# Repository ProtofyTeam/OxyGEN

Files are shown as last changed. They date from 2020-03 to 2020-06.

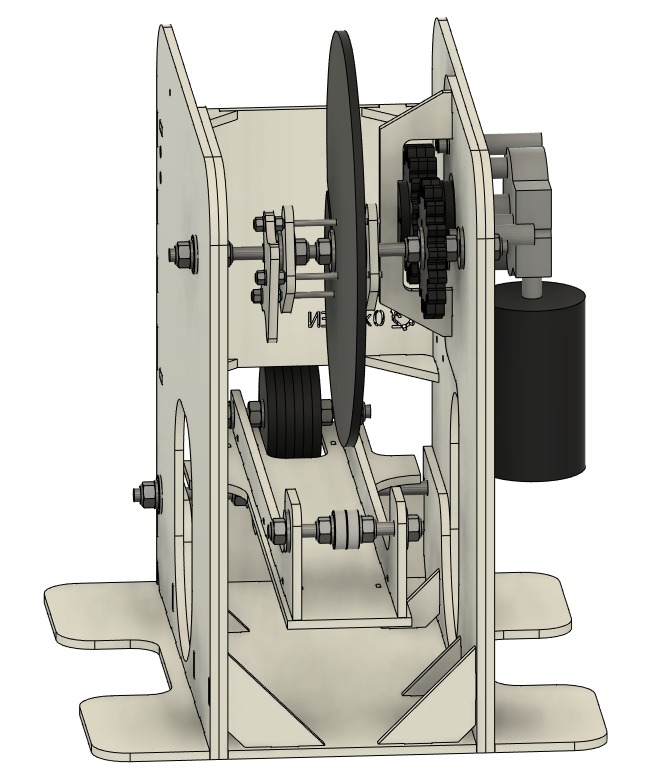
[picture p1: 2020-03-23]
oxygen_M/OxygenM_V5/OxygenM_V5 5mm/Images/f347e17a-e1d2-4af8-affd-06b3623857e8.jpeg

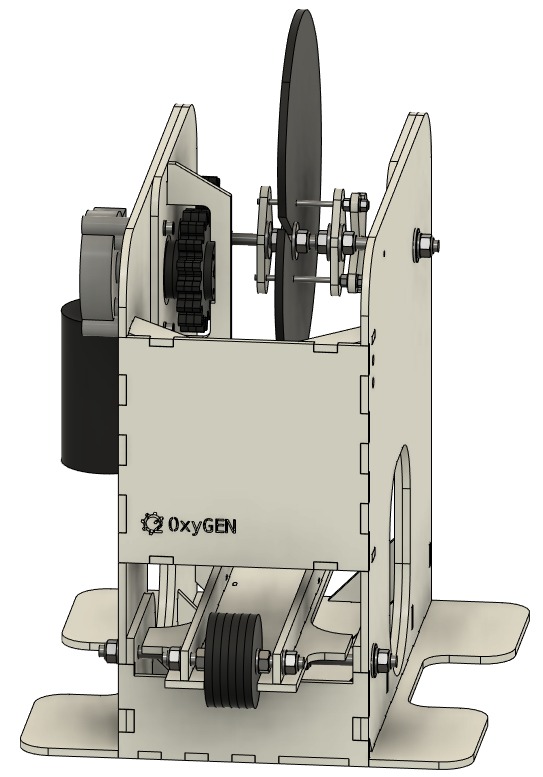
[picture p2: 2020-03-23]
oxygen_M/OxygenM_V5/OxygenM_V5 5mm/Images/4b5abb1e-1ea3-4c3a-8013-bc336fb86296.jpeg

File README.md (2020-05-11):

# OxyGEN

OxyGEN is a collaborative hardware project started and led by [Protofy.xyz](https://protofy.xyz/), a Barcelona-based company that supports innovation within Corps and SME’s by developing hardware and software solutions.

Our mission is to offer a chance of survival to those who are denied access to an artificial ventilator due to shortage of supply.

To fulfill this mission, OxyGEN created an open hardware, low cost and low tech emergency respirator using a manual resuscitator for emergency situations contributing to save lives.

There are 2 different versions of OxyGEN. The maker version "OxyGEN-M" and the industrial version "OxyGEN-IP".

* **OxyGEN-M** is designed for makers and can be built using common tools and no special machinery or materials are needed. 

* **OxyGEN-IP** is the version for industrial scale production. Foldforming metalworking machinery and engineering knowledge is needed to build OxyGEN-IP.

OxyGEN-IP has sucessfully passed clinical tests "in vitro" and "in vivo".

OxyGEN-IP has received authorization from the AEMPS to be used in clinical investigation in Hospital Clinic and Hospital Germans Trias i Pujol.

All content is licensed under the [CC by SA](https://creativecommons.org/licenses/by-sa/3.0)

**Important notice**

**OxyGEN is not a certified medical device. Always use OxyGEN under the supervision of qualified medical personnel. Incorrect use of the machine can result in serious injury or death.**

You can find all the information available on our [web](https://www.oxygen.protofy.xyz/?lang=es)

You can also find us at [Discord](https://discord.gg/yyYQxEG)

For any other questions, you can write to us at oxygen@protofy.xyz

-------------------------------------------------------------------------------------

OxyGEN es un proyecto colaborativo de hardware empezado y liderado por [Protofy.xyz](https://protofy.xyz/), una compañía barcelonesa que da soporte a la innovación en grandes empresas y Pymes desarrollando soluciones de hardware y software.

Nuestra misión es ofrecer una oportunidad de supervivencia a aquellos a los que se les ha denegado el acceso a un ventilador artificial debido a la escasez de suministro.

Para lograr esta misión, OxyGEN ha creado un respirador de emergencia de hardware libre, bajo coste y baja tecnología usando un resucitador manual para situaciones de emergencia, contribuyendo a salvar vidas.

Hay dos versiones diferentes de OxyGEN. La versión maker "OxyGEN-M" y la versión industrial "OxyGEN-IP".

* **OxyGEN-M** ha sido diseñado para ser construido por makers. No se necesitan herramientas especiales ni materiales caros. 

* **OxyGEN-IP** es la versión diseñada para la producción industrial a gran escala. Se necesita maquinaria industrial y conocimientos de ingeniería para construirla. 

OxyGEN-IP ha pasado satisfactoriamente pruebas de laboratorio "in vitro" e "in vivo". 

OxyGEN-IP ha recibido autorización de la AEMPS para su uso en estudios clínicos en el Hospital Clinic y el Hospital Germans Trias i Pujol.

Todo el contenido esta bajo licencia [CC by SA](https://creativecommons.org/licenses/by-sa/3.0)

**Nota Importante**

**OxyGEN no es un dispositivo médico certificado. No use OxyGEN sobre una persona, excepto bajo supervisión y aprobación médica. El uso incorrecto del aparato puede provocar lesiones graves o incluso la muerte. Usar OxyGEN en su país podría ser ilegal.**

Puedes encontrar toda la información disponible en nuestra [web](https://www.oxygen.protofy.xyz/?lang=es)

También puedes encontrarnos en [Discord](https://discord.gg/yyYQxEG)

Para cualquier otra consulta, puedes escribirnos a oxygen@protofy.xyz

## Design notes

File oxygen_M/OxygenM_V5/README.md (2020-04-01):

# OxyGEN V5

Mejoras:

- posibilidad de cambiar fácilmente las levas, para configurar los ritmos a respiraciones a diferentes tipos de pacientes

- integración de un DIMMER de leds que permite regular la velocidad del motor, para no depender los parámetros de cada motor en específico y poder ajustarlo a necesidades de paciente

- uso validado de un simple alimentación de PC (fuente ATX, 12v)

- varias horas de funcionamiento en continuo, comprobando la durabilidad del sistema

------------------------------------------------------------------------------------

Improvements:

- possibility to easily change the cams, to configure the rhythms to breaths for different types of patients

- integration of a LED DIMMER that allows regulating the motor speed, so as not to depend on the parameters of each specific motor and to be able to adjust it to patient needs

- validated use of a simple PC power supply (ATX source, 12v)

- several hours of continuous operation, checking the durability of the system

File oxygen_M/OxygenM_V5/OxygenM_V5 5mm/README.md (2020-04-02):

# OxyGEN V5 5mm

Diseño original de OxyGEN en 5mm

Esta version puede ser fabricada en acrilico, madera, chapa, o cualquier otro material rigido de 5mm que tenga suficiente resistencia como para aguantar la maquina y sus componentes.

Los planos estan diseñados para corte laser

------------------------------------------------------------------------------------

Original OxyGEN design in 5mm

This version can be made of acrylic, wood, sheet metal, or any other rigid 5mm material that has enough resistance to support the machine and its components.

The blueprints are designed for laser cutting

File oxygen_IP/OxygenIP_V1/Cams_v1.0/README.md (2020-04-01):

* XS = 450mL
* S = 500 mL
* M = 550 mL
* L = 600 mL
* XL = 650 mL

Se han publicado 3 sets de levas con relaciones de inspiración-espiración diferentes expresado como 1:N.

Set 1: Ratio 1:1

Set 2: Ratio 1:2

Set 3: Ratio 1:3

*En un pulmón sano y sin PEEP.

**Con una PEEP de 10 cm H2O una resistencia de 20 mbar/L/s y una complianza de 30 mL/mbar (valores para un pulmón muy dañado) los valores se verán reducidos en aproximadamente 120 mL

------------------------------------------------------------

3 sets of cams had been published with different inspiration-expiration time rates. Expressed as 1:N

Set 1: Rate 1:1

Set 2: Rate 1:2

Set 3: Rate 1:3

*In a healthy lung without PEEP.

**With a PEEP of 10 cm H2O a resistance of 20 mbar / L / s and a compliance of 30 ml / mbar (values for a badly damaged lung) the values will be reduced by approximately 120 ml

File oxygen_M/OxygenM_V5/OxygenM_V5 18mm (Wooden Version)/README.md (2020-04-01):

# OxyGEN V5 18mm

Se trata del diseño original V5 adaptado para ser fabricado con tablero de madera para poder fabricarlo con herramientas manuales y herrajes faciles de encontrar.

---------------------------------------------------

This is the original V5 design adapted to be made of wooden board so that it can be made with hand tools and easy-to-find hardware.

by Suso Caamanho

https://www.paoson.com/es/blog/respirador-manual-automatizado-n137

https://www.facebook.com/paosonwoodwork

https://www.youtube.com/user/gpaoson

https://www.instagram.com/paoson_woodworking/

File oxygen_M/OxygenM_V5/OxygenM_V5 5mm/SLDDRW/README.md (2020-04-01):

# OxyGEN v5 5mm version SLDDRW

Thanks to Neco!
https://www.linkedin.com/in/neco-garcía-quintanilla-690080166/

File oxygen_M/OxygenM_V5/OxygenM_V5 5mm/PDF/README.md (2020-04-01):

# OxyGEN v5 5mm version PDF's

Thanks to Neco!
https://www.linkedin.com/in/neco-garcía-quintanilla-690080166/

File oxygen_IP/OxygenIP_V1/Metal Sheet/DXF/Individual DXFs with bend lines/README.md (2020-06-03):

# Individual DXFs with bend lines

These are DXFs of the individual sheet metal parts with bend lines added for the bent parts.  The bend lines are on a separate layer named **Bending**.

One thing that was slightly changed from the originals was that the sets of three holes for the hinges on the **Outer Cover** and **Upper Cover** were moved 0.060 inch (1.52 mm) farther from the bend line to prevent the holes from "puckering" when the parts were bent.

These DXFs were created by [Kooima Company](https://www.kooimacompany.com/) for parts that were manufactured for the [Ventila](https://ventila.org/) organization in New York.

One thing to note is that, since metric thicknesses of stainless steel sheet are not so common in the USA, the following material substitutions were made:

**1mm:** Used 20 GA stainless steel (0.0375 in) (0.9525 mm)

**3mm:** Used 11 GA stainless steel (0.1250 in)	(3.175 mm)

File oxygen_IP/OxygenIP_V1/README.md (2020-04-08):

# OxyGEN IP V1.0

This version of OxyGEN is designed to be massively produced by manufactures willing to help.

------------------------------------------------------------------

Esta versión de OxyGEN está diseñada para ser producida masivamente por fabricantes dispuestos a ayudar.

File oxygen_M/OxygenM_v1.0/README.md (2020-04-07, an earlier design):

# OxyGEN V1.0

Primera versión de OxyGEN

Esta versión está pensada para producirse con herramientas de corte de madera básicas (sierra de mano, caladora...), usando madera de 20mm

-------------------------------------------

First version of OxyGEN

This version is designed to be produced with basic wood cutting tools (hand saw, jigsaw ...), using 20mm wood.

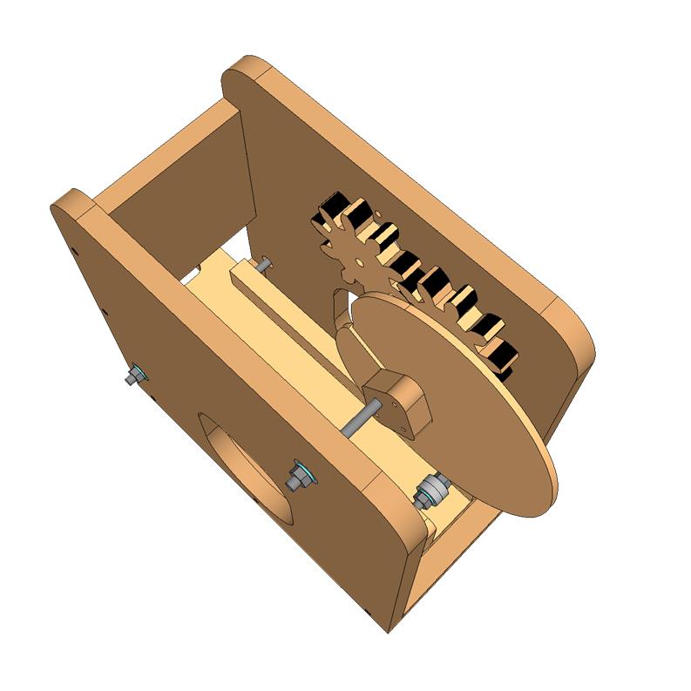
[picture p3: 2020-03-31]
oxygen_M/OxygenM_V5/OxygenM_V5 18mm (Wooden Version)/Photo/OxyGEN-master_Madera_Photo 2.jpg

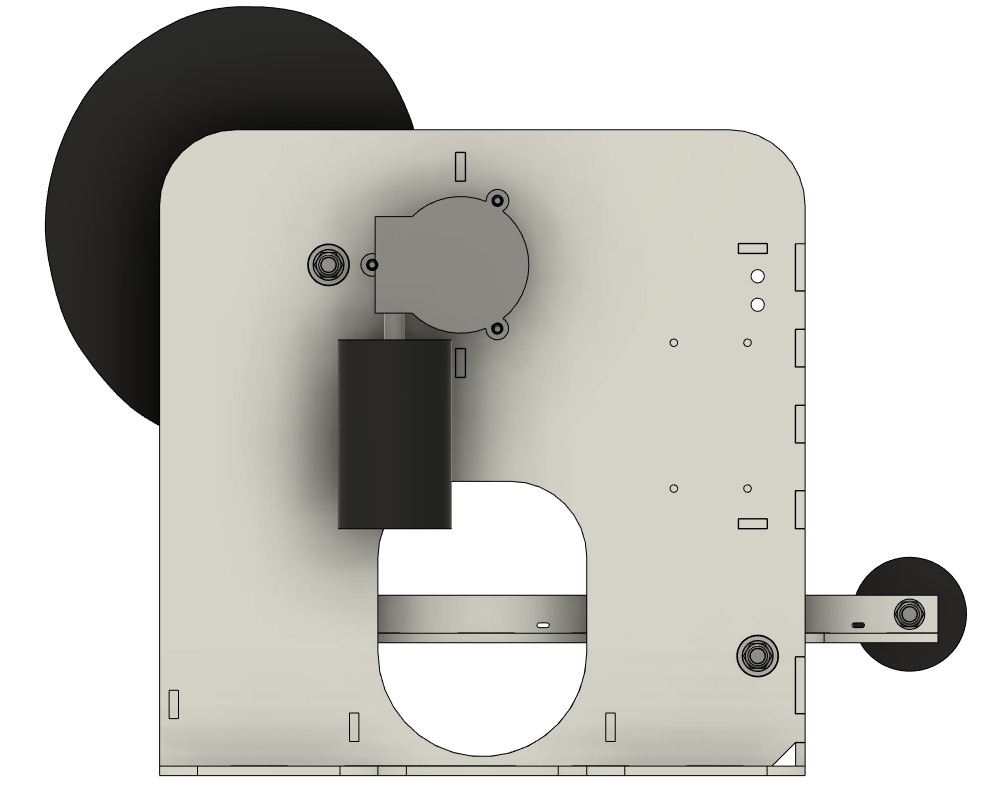
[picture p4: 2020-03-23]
oxygen_M/OxygenM_V5/OxygenM_V5 5mm/Images/67442de0-a628-4195-af0d-b7cb26ab55f8.jpeg

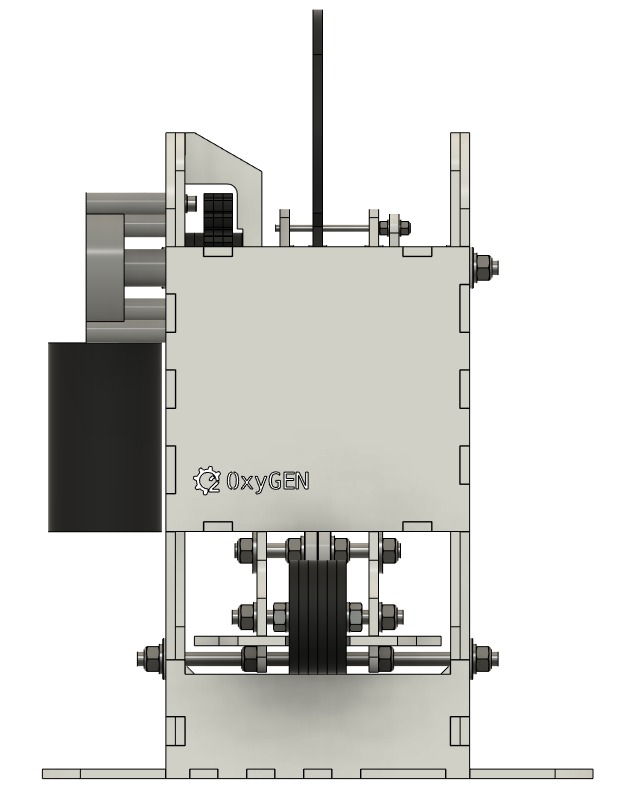
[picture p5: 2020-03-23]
oxygen_M/OxygenM_V5/OxygenM_V5 5mm/Images/628c36c9-1eaf-4945-878f-27b9a3d66050.jpeg

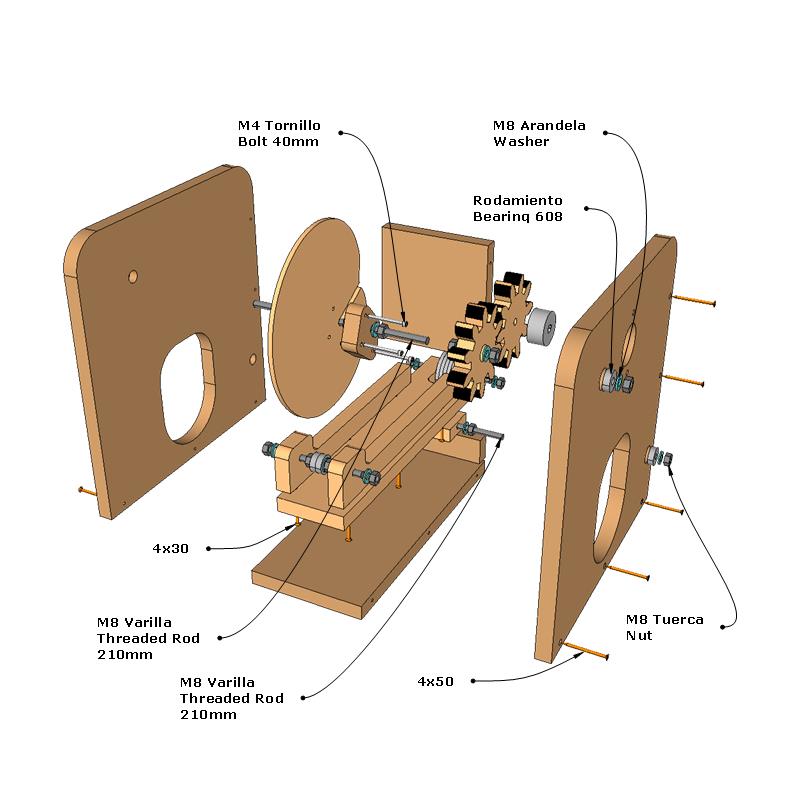
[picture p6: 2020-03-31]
oxygen_M/OxygenM_V5/OxygenM_V5 18mm (Wooden Version)/Photo/OxyGEN-master_Madera_Fasteners.jpg

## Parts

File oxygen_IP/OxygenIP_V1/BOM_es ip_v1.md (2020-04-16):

# Lista de materiales necesarios para IP_v1:

* 1	Chapa Inox 1 mm	
* 1	Chapa Inox 3 mm	
* 1	Chapa Inox 5 mm	
* 1	Plancha Metacrilato 5 mm x 485,5 mm x 160 mm	
* 1	Plancha Nylon/Delrin/PVC 10 mm x 50 mm x 42 mm	
* 1	Barra Inox Ø12 mm x 158 mm 	
* 1	Barra Inox Ø16 mm x 170 mm	
* 1	Barra Inox Ø50 mm x 20 mm	
* 1	Barra Nylon/Delrin Ø10,5 mm x 51 mm
* 3	Barra Nylon/Delrin Ø12 mm x 43,5 mm	
* 1	Barra Nylon/Delrin Ø22 mm x 105 mm	
* 1	Barra Nylon/Delrin Ø50 mm x 52 mm	
* 1	Liston Nylon/Delrin 42 mm x 33 mm x 105 mm	
* 1	Liston Nylon/Delrin 70 mm x 24,8 mm x 305 mm	
* 2	Pasador Metálico Ø6 mm x 23 mm	
* 1	Manómetro	
* 4	Rodamiento Ø37 mm x 12 mm	
* 1	Motor 12V 48W 6Nm 30RPM REF.11194592000E	
* 1	Fuente PC ATX 500W	
* 1	Dimmer LED 12/24V 8A	
* 2	Final de carrera	
* 1	Luz de funcionamiento 230V AC 5W	
* 1	Tapón Ø40 mm	
* 1	Diodo Schottky Imax ≥ 5 A, Pd(25ºC) ≥ 5 W	
* 1	Conector Alimentación IEC C14 con Interruptor y Fusible	
* 1	Cable Alimentación IEC C13 a Faston	
* 1	Cable AWG 16 Aprox. 1 m	
* 6	Tuerca M3 	
* 7	Tuerca M5	
* 5	Tuerca Remachada M5	
* 2	Tapex M10
* 2	Tornillo DIN 912 M3 x 15 mm	
* 4	Tornillo DIN 912 M3 x 16 mm	
* 1	Tornillo DIN 912 M5 x 40 mm	
* 3	Tornillo DIN 912 M6 x 50 mm	
* 4	Tornillo M6 x 24 mm	
* 2	Tornillo M10 x 20 mm	
* 6	Tornillo Roscachapa M4 x 10 mm	
* 12 	Tornillo Roscachapa M5 x 12	mm
* 8	Tornillo Roscachapa M5 x 20 mm	
* 47 	Remache Ø4,8 mm
* 1	Hembrilla Rosca Ø4 mm x 18 mm, enganche ØInterior 8 mm	 
* 2	Bisagra 60 mm x 50 mm	
* 1	Muelle ØInterior 9 mm x 90 mm	
* 1	Muelle ØInterno 12mm x 31 mm 	
* 1	Junta Tórica ØExterior 30 mm, ØInterior 22 mm	
* 10 	Separador de goma para agujero Ø15,5, separación 6 mm	
* 1	Separador Nylon ØExterior 20 mm, ØInterior 13 mm, 29 mm	
* 1	Separador Nylon ØExterior 20 mm, ØInterior 13 mm, 35 mm	
* 1	Espuma Aislante 6 mm x 171 mm x 45 mm	
* 2	Goma Protectora Longitud Aprox. 460 mm 	
* 2	Goma Protectora Grosor 2.5 mm Longitud Aprox. 1125 mm	
* 1	Acoplador del Motor de Ø12 mm a Ø10 mm, longitud 35 mm	
* 1	Casquillo de Bronce Ø16 mm x 70 mm

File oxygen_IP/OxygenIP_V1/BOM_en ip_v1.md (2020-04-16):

# Bill Of Material for  IP_v1:

* 1	Inox Sheet 1 mm	
* 1	Inox Sheet 3 mm	
* 1	Inox Sheet 5 mm	
* 1	Methacrylate Sheet 5 mm x 485,5 mm x 160 mm	
* 1	Nylon/Delrin/PVC Sheet 10 mm x 50 mm x 42 mm	
* 1	Inox Bar Ø12 mm x 158 mm 	
* 1	Inox Bar Ø16 mm x 170 mm	
* 1	Inox Bar Ø50 mm x 20 mm	
* 1	Nylon/Delrin Bar Ø10,5 mm x 51 mm
* 3	Nylon/Delrin Bar Ø12 mm x 43,5 mm	
* 1	Nylon/Delrin Bar Ø22 mm x 105 mm	
* 1	Nylon/Delrin Bar Ø50 mm x 52 mm	
* 1	Nylon/Delrin Batten 42 mm x 33 mm x 105 mm	
* 1	Nylon/Delrin Batten 70 mm x 24,8 mm x 305 mm	
* 2	Metal Pin Ø6 mm x 23 mm	
* 1	Manometer	
* 4	Bearing Ø37 mm x 12 mm	
* 1	Motor 12V 48W 6Nm 30RPM REF.11194592000E	
* 1	PC Power Supply ATX 500W	
* 1	Dimmer LED 12/24V 8A	
* 2	Micro Switch
* 1	Operating Light 230V AC 5W	
* 1	Plug Ø40 mm	
* 1	Schottky Diode Ifmax ≥ 5 A, Pd(25ºC) ≥ 5 W	
* 1	Power Connector IEC C14 with Switch and Fuse	
* 1	Power Cable IEC C13 to Faston	
* 1	Cable AWG 16 Approx. 1 m	
* 6	Nut M3 	
* 7	Nut M5	
* 5	Rivet Nut M5	
* 2	Tapex M10
* 2	Screw DIN 912 M3 x 15 mm	
* 4	Screw DIN 912 M3 x 16 mm	
* 1	Screw DIN 912 M5 x 40 mm	
* 3	Screw DIN 912 M6 x 50 mm	
* 4	Screw M6 x 24 mm	
* 2	Screw M10 x 20 mm	
* 6	Self Tapping Screw M4 x 10 mm	
* 12 	Self Tapping Screw M5 x 12 mm
* 8	Self Tapping Screw M5 x 20 mm	
* 47 	Rivet Ø4,8 mm
* 1	Eyebolt Thread Ø4 mm x 18 mm, hitch ØIn 8 mm	 
* 2	Hinge 60 mm x 50 mm	
* 1	Spring ØIn 9 mm x 90 mm	
* 1	Spring ØIn 12mm x 31 mm 	
* 1	O-ring ØEx 30 mm, ØIn 22 mm	
* 10 	Rubber hole spacer Ø15,5, separation 6 mm	
* 1	Nylon Spacer ØEx 20 mm, ØIn 13 mm, 29 mm	
* 1	Nylon Spacer ØEx 20 mm, ØIn 13 mm, 35 mm	
* 1	Foam 6 mm x 171 mm x 45 mm	
* 2	Protective rubber length Approx. 460 mm 	
* 2	Protective rubber thickness 2.5 mm length Approx. 1125 mm	
* 1	Motor coupling from Ø12 mm to Ø10 mm, length 35 mm	
* 1	Bronze Bearing Ø16 mm x 70 mm

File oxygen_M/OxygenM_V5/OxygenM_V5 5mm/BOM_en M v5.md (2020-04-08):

#Bill Of Material for V5M:

 * 2 threaded rod M8 190mm
 * 2 M8 90mm threaded rod
 * 3 threaded rod M4 71mm
 * 21 Locking nut M8
 * 2 Nut M8
 * 10 M8 washer
 * 12 M8 wide washer
 * 10 Locking nut
 * 14 M4 washer
 * 3 M6 15mm Screw
 * 3 M6 washer
 * 6 Bearing 22m
 * 12 / 24V LED dimmer with 8A max.
 * Wiper motor 12v 48W 6Nm 30rpm max (We have used the DOGA model 11194592000E)
 * PC ATX 500w source
 * Super glue
 * Imax Diode> = 150A Pd (25º)> = 5W
 * 1m AWG 16 Cable
 * Acrylic sheet 5mm 0.95m x 1.2m

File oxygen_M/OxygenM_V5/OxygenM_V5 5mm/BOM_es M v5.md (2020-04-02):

# Lista de materiales necesarios para V5M:

 * 2 varilla roscada M8 190mm
 * 2 varilla roscada M8 90mm
 * 3 varilla roscada M4 71mm
 * 21 Tuerca bloqueante M8
 * 2 Tuerca M8 
 * 10 Arandela M8
 * 12 Arandela ancha M8
 * 10 Tuerca bloqueante
 * 14 Arandela M4
 * 3 Tornillo M6 15mm
 * 3 Arandela M6
 * 6 Rodamiento 22m
 * Dimmer LED 12/24V con 8A max
 * Motor limpiaparabrisas 12v 48W 6Nm 30rpm max (Nosotros hemos usado el modelo 11194592000E de DOGA)
 * Fuente PC ATX 500w
 * Superglue
 * Diodo Imax >= 150A Pd(25º)>= 5W
 * 1m Cable AWG 16
 * Plancha metacrilato 5mm 0.95m x 1.2m

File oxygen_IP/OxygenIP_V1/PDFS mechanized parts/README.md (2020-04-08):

Muchas gracias a nuestros amigos de OxyGEN Brasil!

https://www.facebook.com/Volunt%C3%A1rios-An%C3%B4nimos-Ventilador-Oxygen-110522390598983

------------------------------------------------------------------

Thank you very much to our friends from OxyGEN Brazil!

https://www.facebook.com/Volunt%C3%A1rios-An%C3%B4nimos-Ventilador-Oxygen-110522390598983

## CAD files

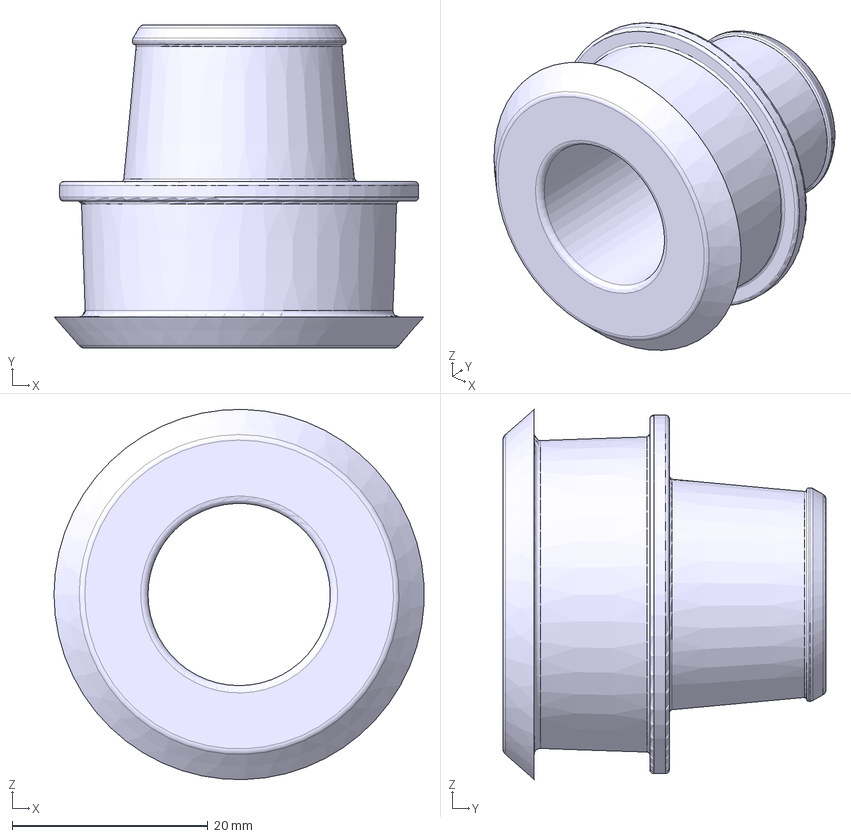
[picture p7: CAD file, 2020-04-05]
accessories/spur back to tube.step
37.8 x 33.0 x 37.8 mm

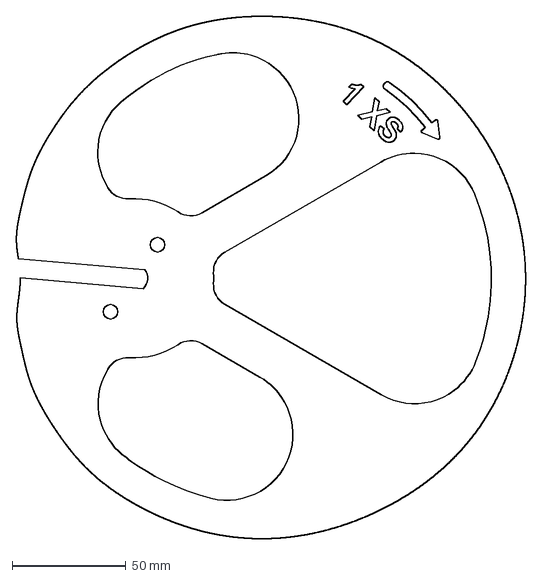
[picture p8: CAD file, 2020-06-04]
oxygen_IP/OxygenIP_V1/Cams_v1.0/Set 1/1-1 89-205-50-XS-v8.dxf
223.9 x 229.8 mm

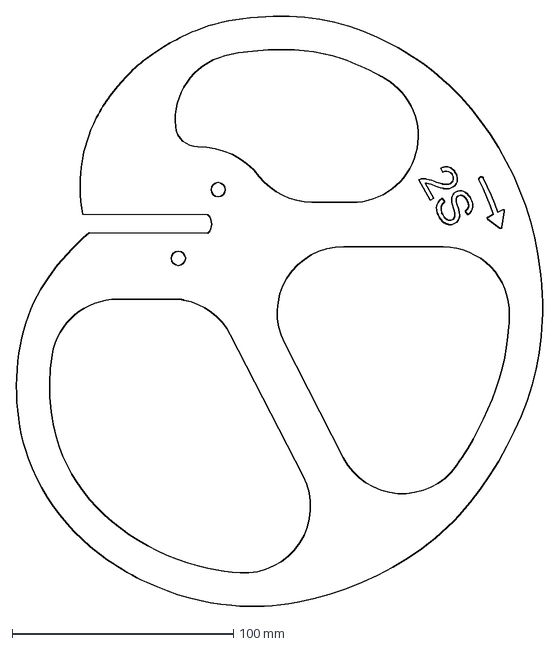
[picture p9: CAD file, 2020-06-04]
oxygen_IP/OxygenIP_V1/Cams_v1.0/Set 2/1-2 83-205-50-S-v8.dxf
238.2 x 267.0 mm

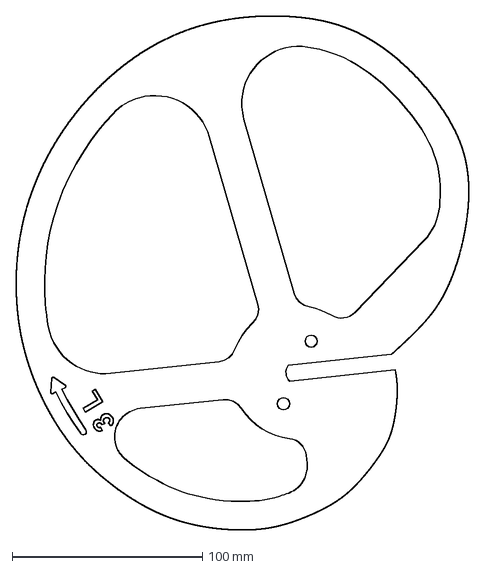
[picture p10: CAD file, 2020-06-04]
oxygen_IP/OxygenIP_V1/Cams_v1.0/Set 3/1-3 71-205-50-L-v8.dxf
238.1 x 270.3 mm

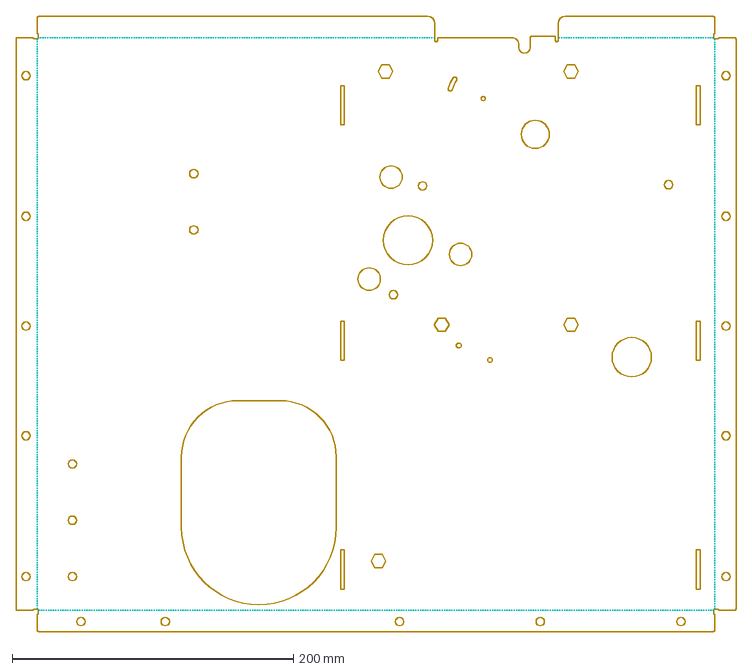
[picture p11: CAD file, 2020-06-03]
oxygen_IP/OxygenIP_V1/Metal Sheet/DXF/Individual DXFs with bend lines/1mm/Central Cover.dxf
511.8 x 437.3 mm

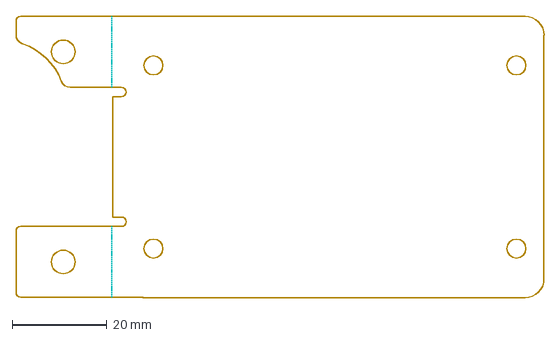
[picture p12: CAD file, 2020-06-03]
oxygen_IP/OxygenIP_V1/Metal Sheet/DXF/Individual DXFs with bend lines/3mm/Dimmer Support.dxf
111.7 x 59.5 mm

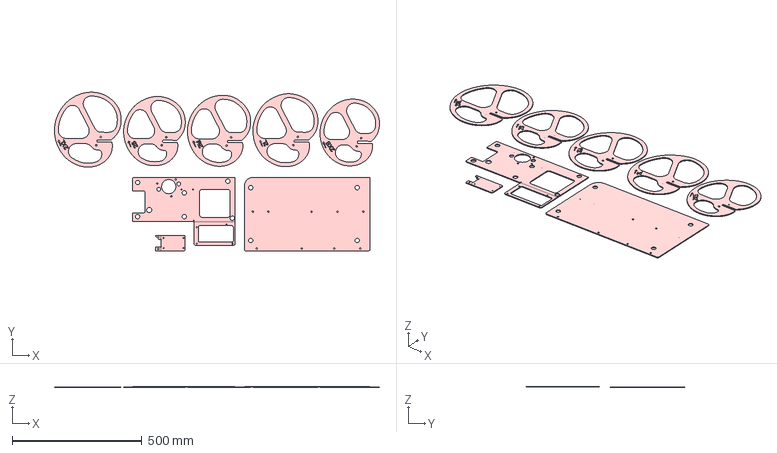
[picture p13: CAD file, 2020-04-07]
oxygen_IP/OxygenIP_V1/Metal Sheet/STEP/Oxygen-IP V14.4 Metal Sheet 3 mm Parts.step
1253.3 x 611.8 x 5.00 mm

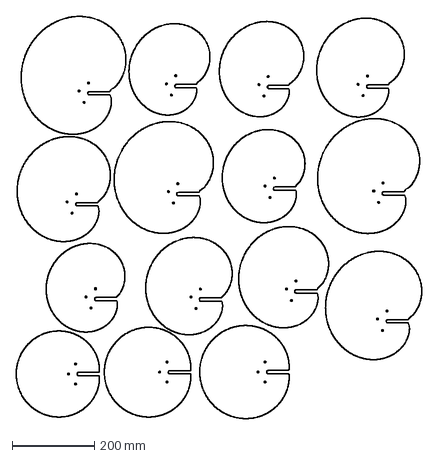
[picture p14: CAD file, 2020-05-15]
oxygen_M/OxygenM_V5/OxygenM_V5 5mm/cams/OXyGEN_V5_M_cams.dxf
983.3 x 975.3 mm

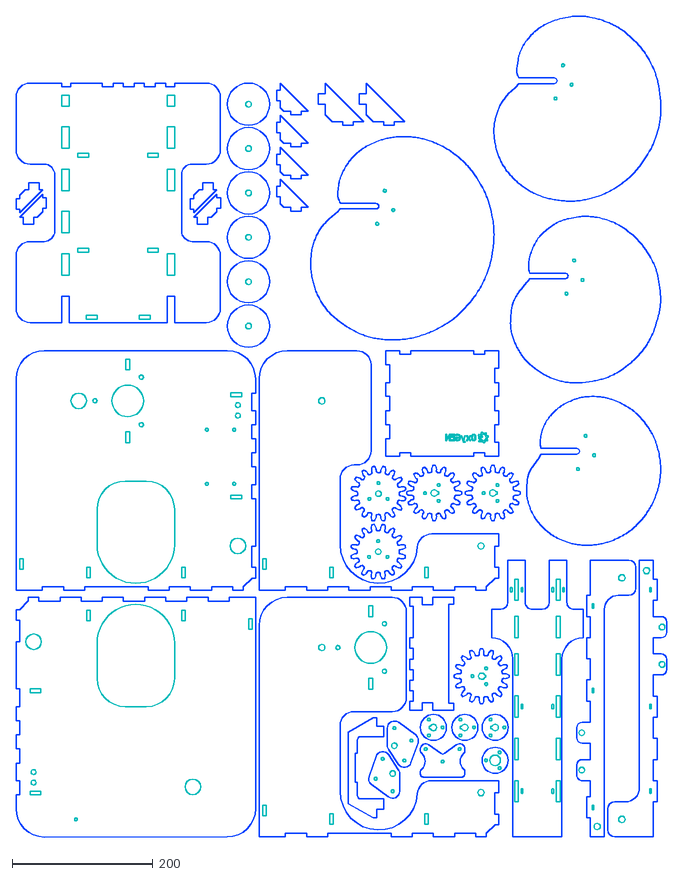
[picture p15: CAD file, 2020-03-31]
oxygen_M/OxygenM_V5/OxygenM_V5 5mm/DXF/OxyGEN_Maker_V5.dxf
924.0 x 1165.5

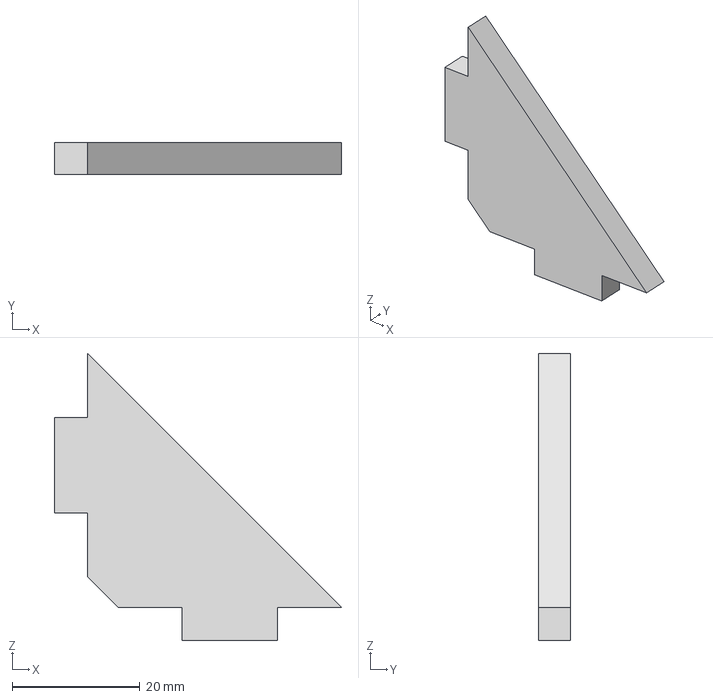
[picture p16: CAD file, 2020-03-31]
oxygen_M/OxygenM_V5/OxygenM_V5 5mm/STEP/Oxygen Maker Escuadra Frontal 4.step
45.0 x 5.00 x 45.0 mm

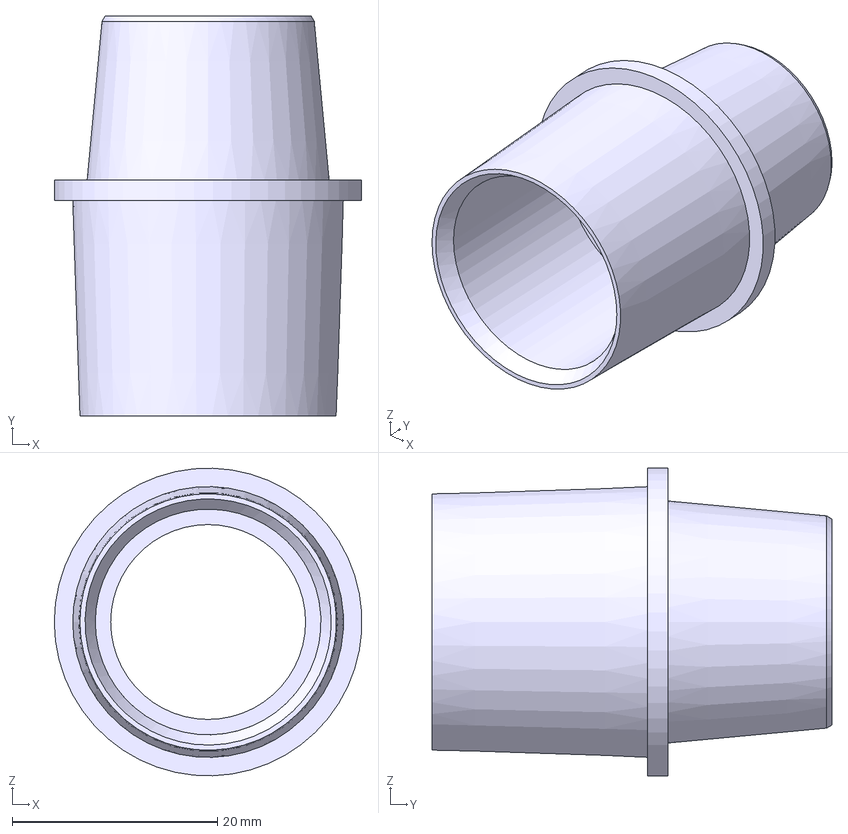
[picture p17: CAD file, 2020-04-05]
accessories/tube to spur valve.step
30.0 x 39.0 x 30.0 mm

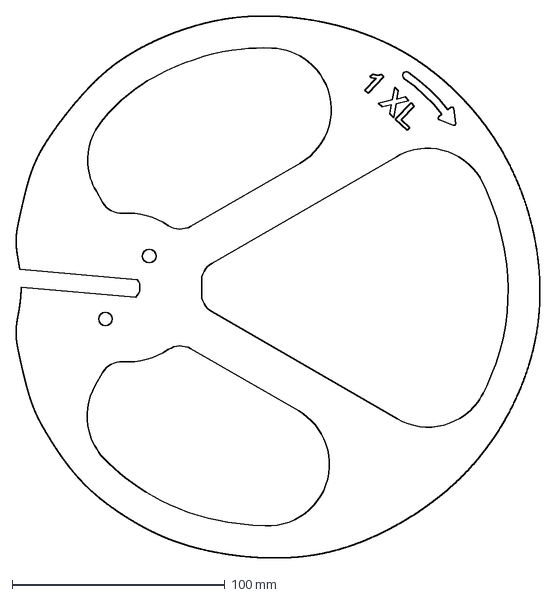
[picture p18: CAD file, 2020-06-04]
oxygen_IP/OxygenIP_V1/Cams_v1.0/Set 1/1-1 65-205-50-XL-v8.dxf
246.5 x 255.0 mm

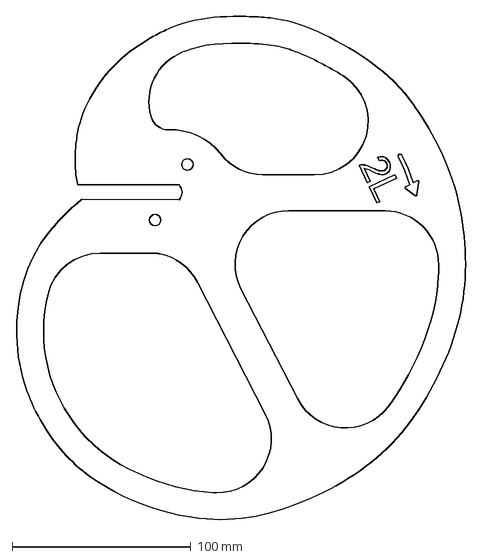
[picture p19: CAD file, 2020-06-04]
oxygen_IP/OxygenIP_V1/Cams_v1.0/Set 2/1-2 71-205-50-L-v8.dxf
251.3 x 281.6 mm

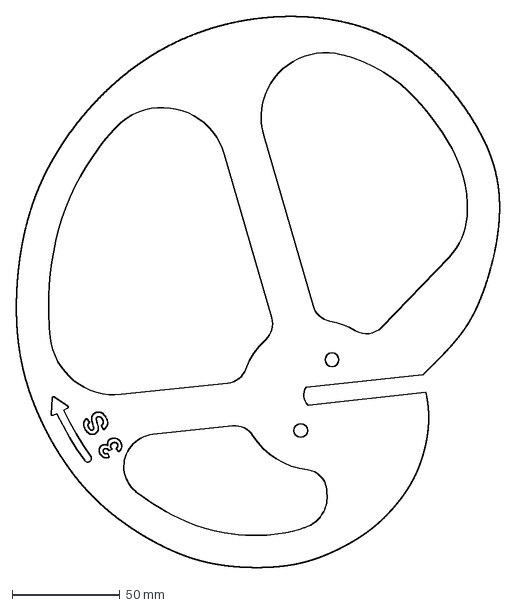
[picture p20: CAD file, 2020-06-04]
oxygen_IP/OxygenIP_V1/Cams_v1.0/Set 3/1-3 83-205-50-S-v8.dxf
224.7 x 256.2 mm

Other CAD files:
oxygen_IP/OxygenIP_V1/Metal Sheet/DXF/Individual DXFs with bend lines/1mm/Upper Cover.dxf
oxygen_IP/OxygenIP_V1/Metal Sheet/DXF/Individual DXFs with bend lines/3mm/Base.dxf
oxygen_IP/OxygenIP_V1/Metal Sheet/STEP/Oxygen-IP V14.4 Metal Sheet 1 mm Parts.step
oxygen_M/OxygenM_V5/OxygenM_V5 5mm/STEP/Oxygen Maker Soporte Pasador 2.step
accessories/Tube to oval valve.step
accessories/tube manometer tube .step
oxygen_IP/OxygenIP_V1/Cams_v1.0/Set 1/1-1 71-205-50-L-v8.dxf
oxygen_IP/OxygenIP_V1/Cams_v1.0/Set 1/1-1 77-205-50-M-v8.dxf
oxygen_IP/OxygenIP_V1/Cams_v1.0/Set 1/1-1 83-205-50-S-v8.dxf
oxygen_IP/OxygenIP_V1/Cams_v1.0/Set 1/Levas_1_1.step
oxygen_IP/OxygenIP_V1/Cams_v1.0/Set 2/1-2 65-205-50-XL-v8.dxf
oxygen_IP/OxygenIP_V1/Cams_v1.0/Set 2/1-2 77-205-50-M-v8.dxf
oxygen_IP/OxygenIP_V1/Cams_v1.0/Set 2/1-2 89-205-50-XS-v8.dxf
oxygen_IP/OxygenIP_V1/Cams_v1.0/Set 2/Levas_1_2.step
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

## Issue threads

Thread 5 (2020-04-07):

### ISSUE TITLE
Please include the quantities of materials required

### ISSUE THREAD

**Issue by dbx834** [ProtofyTeam/OxyGEN#5]
Hello...

It would help if it's included in the [list of requirements](https://github.com/ProtofyTeam/OxyGEN/blob/master/V5/Oxygen%20Maker%20V2/List_Materials_V5M.md) how many units of each item are required to create one machine.

Best
/P

**Comment by HaleTom** [comment]
Broken link above.

New link to V5 list of requirements:
https://github.com/ProtofyTeam/OxyGEN/blob/master/oxygenM/V5/v5%20-%20OxygenProject%205mm/List_Materials_V5M.md

**Comment by HaleTom** [comment]
Equivalent issue en Español:
https://github.com/ProtofyTeam/OxyGEN/issues/2

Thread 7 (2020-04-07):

### ISSUE TITLE
Can not open dxf files with AutoCad 2010

### ISSUE THREAD

**Issue by alanboner** [ProtofyTeam/OxyGEN#7]
AutoCad says:
Unknown value "AC1027" encountered in drawing version.
Invalid or incomplete DXF input -- drawing discarded.

**Comment by SantyG99** [comment]
Do you have the blueprints for AutoCAD? Gretting from Ecuador.

**Comment by alanboner** [comment]
Here are two AutoCAD files from latest drop.  I was able to open the DXF file with Autodesk DWG TrueView. 

 

What material will you be using? 

 

-- Alan

**Comment by alanboner** [comment]
The DWF file for the wood version is attached.

 

Does this work?

**Comment by SantyG99** [comment]
Could you send me to my email directly please i can no get any file sorry, sgomez@ciauto.ec, thank you so much

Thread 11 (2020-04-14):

### ISSUE TITLE
Step-by-step assembly instructions / video

### ISSUE THREAD

**Issue by HaleTom** [ProtofyTeam/OxyGEN#11]
I want to assemble the OxyGEN V5 but so far have the following problems:

* I don't know how many bolts to use (see #5)
* I don't know what lengths of rods to use, and where they go

I live on an island with zero ventilators, and hope to save lives.

I see the following, but it is extremely high level. 

https://github.com/ProtofyTeam/OxyGEN/blob/master/oxygenM/V5/v5%20-%20OxygenProject%205mm/Assembly_OxyGEN_V5M_EN.pdf

Could you please make complete, detailed instructions for assembly, or ideally a video?

**Comment by ap0k4** [comment]
We have added the bom and new documentation about it

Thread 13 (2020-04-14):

### ISSUE TITLE
Please add requirements and specifications documentation

### ISSUE THREAD

**Issue by Jaribeau** [ProtofyTeam/OxyGEN#13]
Hi - thanks for your work on this, and for making the design files readily available!

However, I can't for the life of me find any other documentation. Where are are the specifications you designed to? As a team that is spinning up resources to produce designs in Cambodia, we're vetting every project we come across. Requirements and specifications (i.e. knowing that the device was designed with proper clinical input) is by far the most important part.

Ideally they would be included right in the README, and front and centre on the website.

Thanks!

**Comment by ap0k4** [comment]
Added!

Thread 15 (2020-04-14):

### ISSUE TITLE
Thickness in Cam STEP files is inconsistent

### ISSUE THREAD

**Issue by greg-bakker** [ProtofyTeam/OxyGEN#15]
For the OxyGEN-IP, the thickness of the cams in the STEP files is inconsistent.  
The **Cams_v1.0\Set 1\Levas_1_1.step** file shows the thickness as **4mm**.  
The **Cams_v1.0\Set 2\Levas_1_2.step** file shows the thickness as **3mm**.  
The **Cams_v1.0\Set 3\Levas_1_3.step** shows the thickness as **4mm**.  
For reference, the **Metal Sheet\DXF\Oxygen-IP V14.4 Metal Sheet 3 mm Parts.dxf** file has one set of cams on it which would show that they are **3mm** thick.
Should the cams be **3mm** or **4mm** thick?

**Comment by ap0k4** [comment]
Hello! The thickness will depend on the material with which the cams are made, preferably if they are made of aluminum, 4mm would be better.

Thanks for the warning

**Comment by ap0k4** [comment]
Fixed!

**Comment by greg-bakker** [comment]
Thanks for fixing!  If they are made from 304 Stainless is 3mm sufficient?

**Comment by ap0k4** [comment]
yes, it would be enough 3mm for stainless

**Comment by greg-bakker** [comment]
Great!  Thanks for the reply!

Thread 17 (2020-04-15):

### ISSUE TITLE
How to make different I/E rate

### ISSUE THREAD

**Issue by riyanfile2** [ProtofyTeam/OxyGEN#17]
What should I do with the code, if I want to make another I/E rate. 1:5 for example. because my ventilator doesn't work well. when I use 1:2 cam, the measurement shows 2:1 :(

**Comment by ap0k4** [comment]
616/5000
Hello, what you are saying is quite strange.
- make sure the motor rotates in the correct direction
- make sure that the cam is rotating in the correct direction (that no symmetry has occurred)
- make sure that the measurement method is correct (that you are measuring the air intake and not the output, that the circuit is well closed, etc.)

If you need to calculate the cams with a different ratio, we have an article on the blog that explains it, likewise, varying the ratio would not have to solve the problem that the ratio is giving you the other way around.

https://www.oxygen.protofy.xyz/post/cam-shaft-design

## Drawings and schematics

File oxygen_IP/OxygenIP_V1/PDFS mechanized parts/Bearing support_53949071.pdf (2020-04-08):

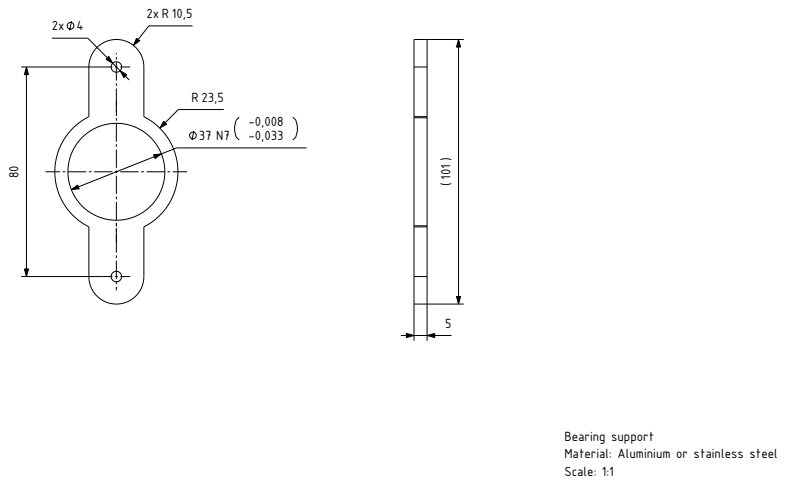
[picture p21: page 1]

Bearing support
Material: Aluminium or stainless steel
Scale: 1:1

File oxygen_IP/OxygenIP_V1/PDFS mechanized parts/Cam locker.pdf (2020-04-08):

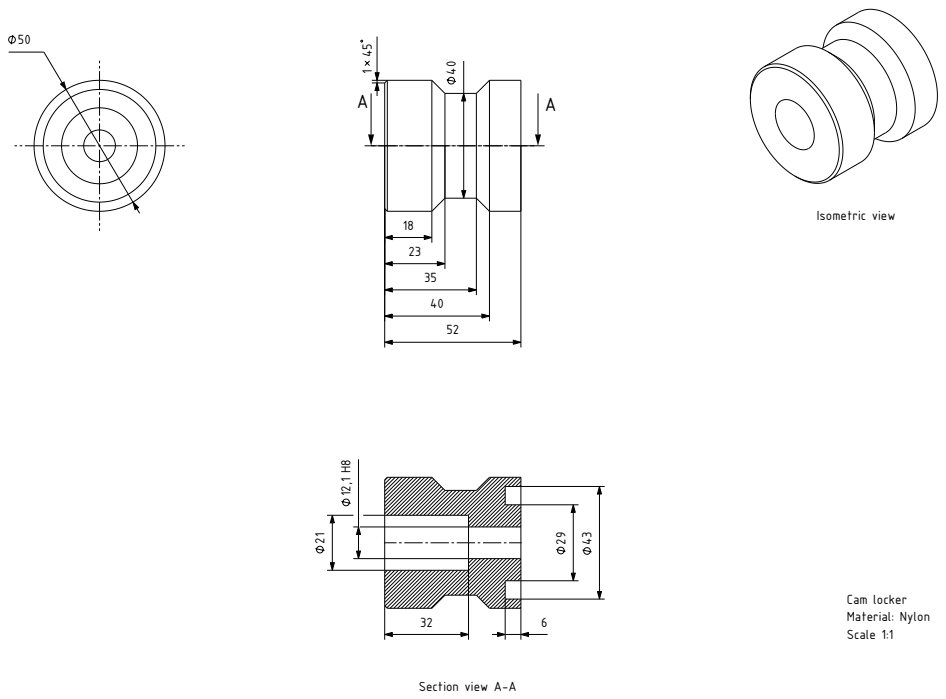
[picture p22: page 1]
Section view A-A; Isometric view; Cam locker Material: Nylon Scale 1:1

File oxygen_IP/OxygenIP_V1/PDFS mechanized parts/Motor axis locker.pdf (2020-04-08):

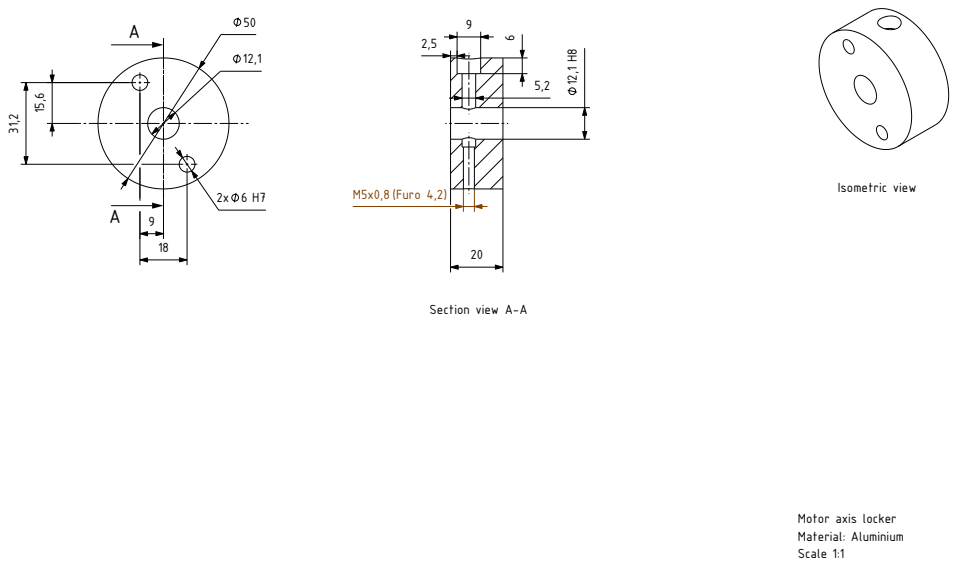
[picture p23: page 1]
M5x0,8 (Furo 4,2); Section view A-A; Isometric view

Motor axis locker
Material: Aluminium
Scale 1:1

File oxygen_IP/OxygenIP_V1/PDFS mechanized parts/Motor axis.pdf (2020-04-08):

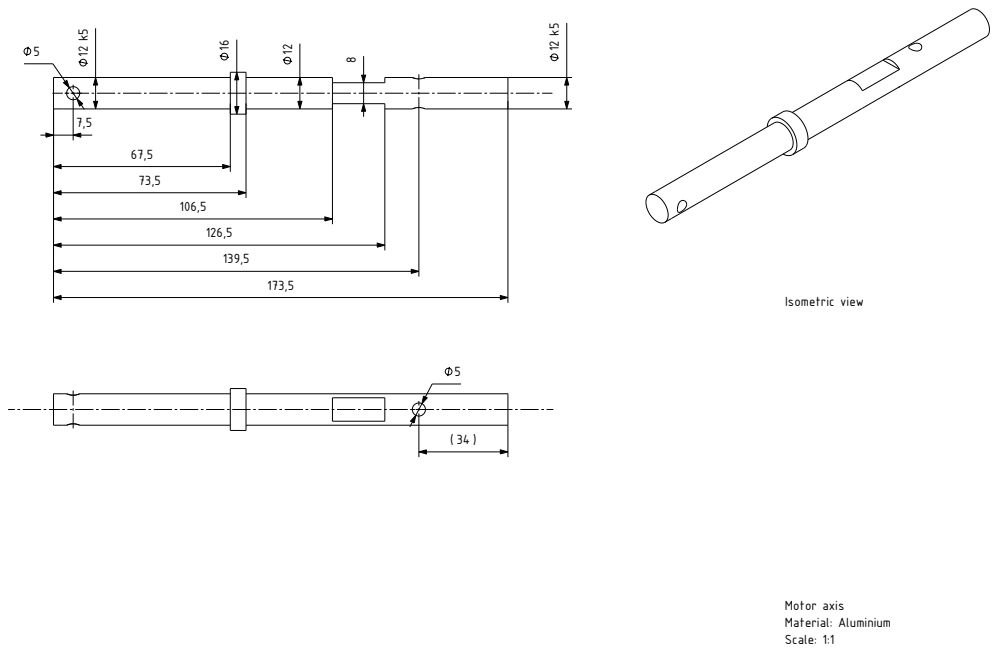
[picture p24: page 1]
Isometric view; Motor axis Material: Aluminium Scale: 1:1

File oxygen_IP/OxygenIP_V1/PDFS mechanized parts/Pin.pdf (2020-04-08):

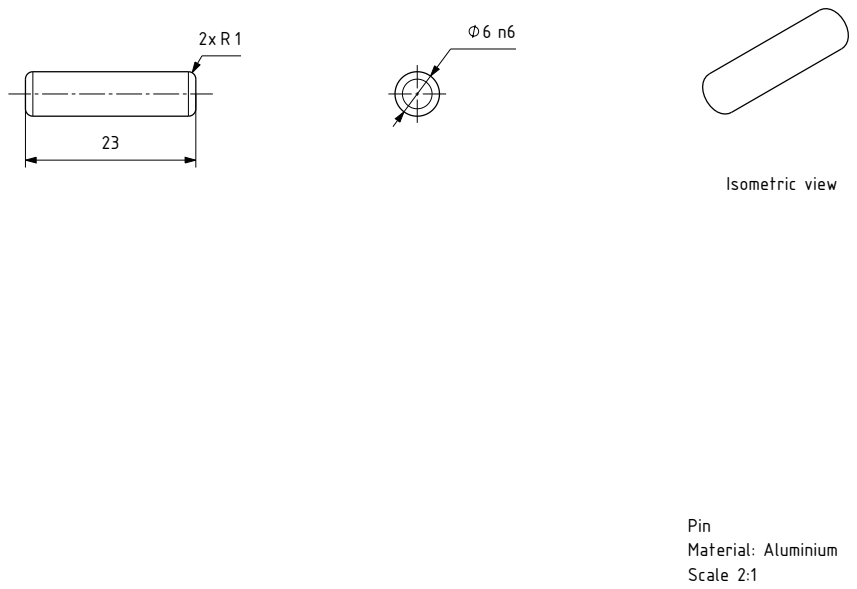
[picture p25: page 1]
Isometric view; Material: Aluminium Scale 2:1

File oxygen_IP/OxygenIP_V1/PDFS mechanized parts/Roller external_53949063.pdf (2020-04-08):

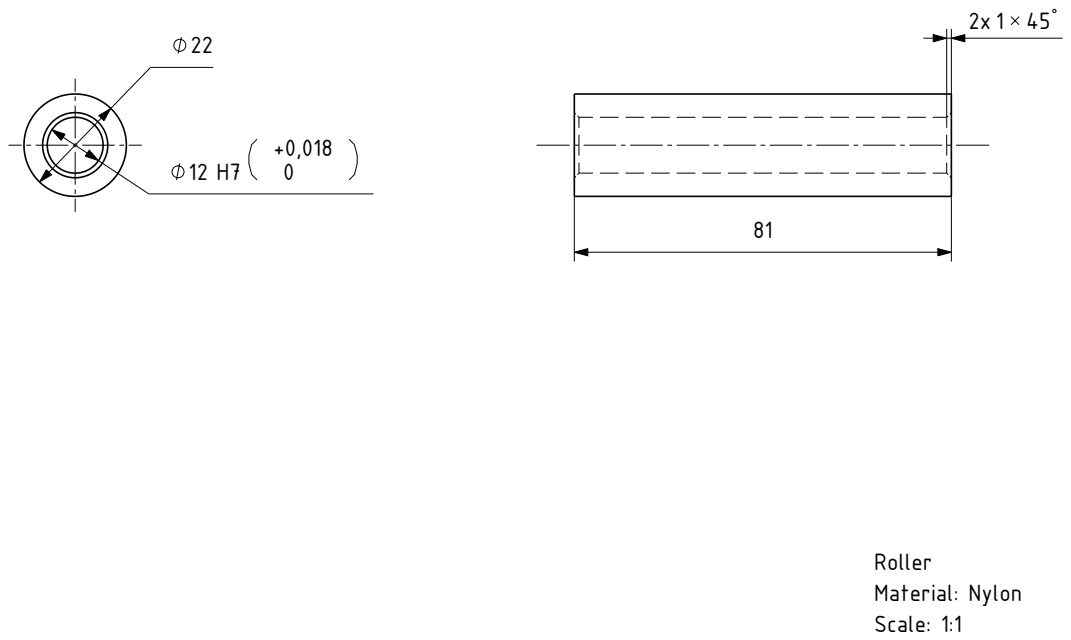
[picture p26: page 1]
Material: Nylon Scale: 1:1

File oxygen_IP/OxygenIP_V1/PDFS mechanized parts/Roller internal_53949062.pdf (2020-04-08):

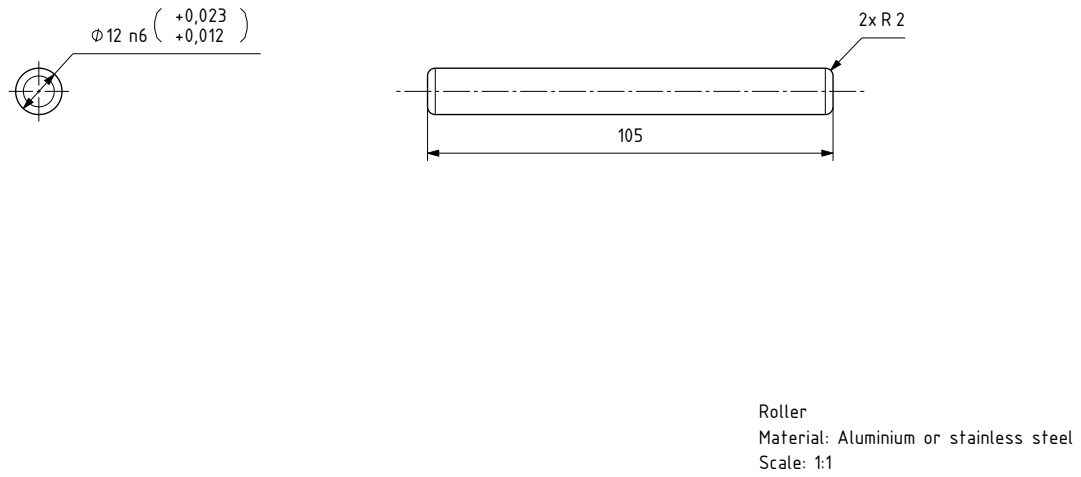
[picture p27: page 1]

Roller
Material: Aluminium or stainless steel
Scale: 1:1

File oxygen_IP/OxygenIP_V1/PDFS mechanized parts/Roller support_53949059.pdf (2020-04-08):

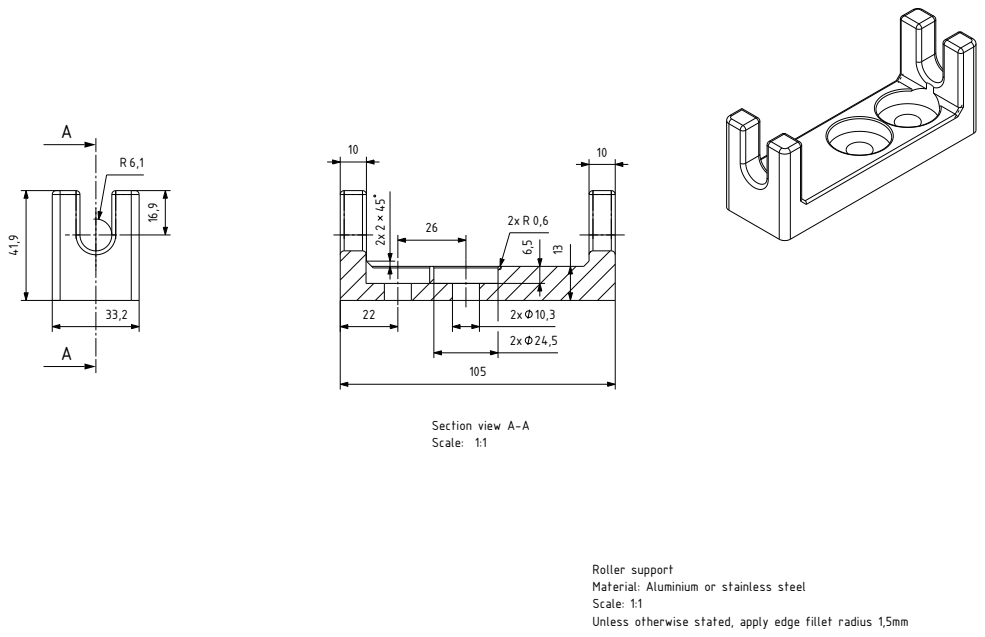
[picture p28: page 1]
Section view A-A Scale: 1:1

Roller support
Material: Aluminium or stainless steel
Scale: 1:1
Unless otherwise stated, apply edge fillet radius 1,5mm

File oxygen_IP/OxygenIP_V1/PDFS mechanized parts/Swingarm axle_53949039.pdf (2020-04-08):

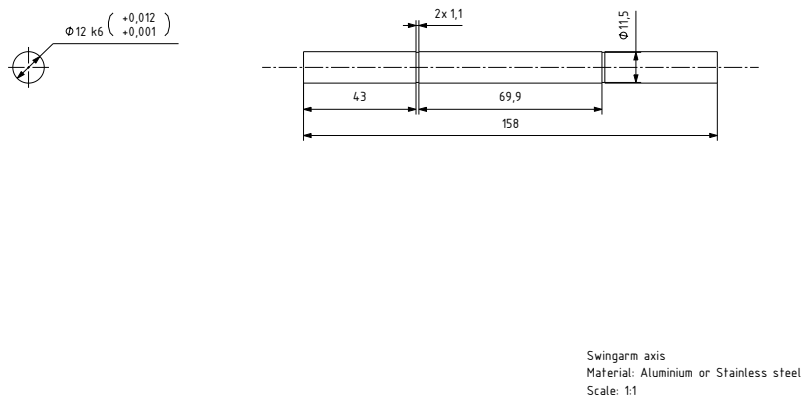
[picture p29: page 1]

Swingarm axis
Material: Aluminium or Stainless steel
Scale: 1:1

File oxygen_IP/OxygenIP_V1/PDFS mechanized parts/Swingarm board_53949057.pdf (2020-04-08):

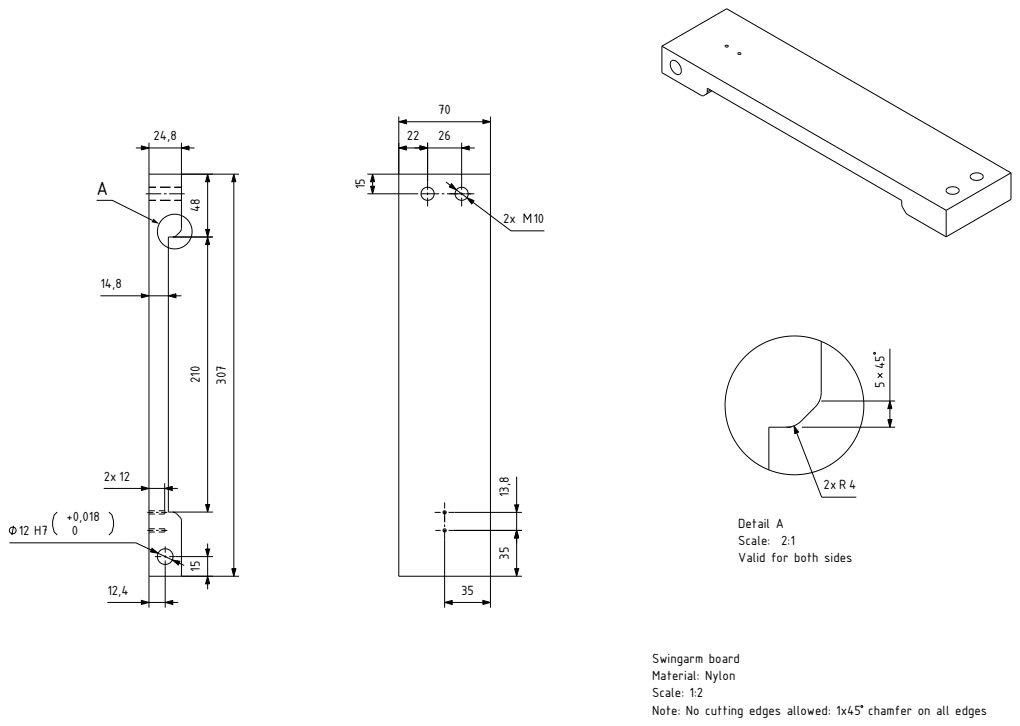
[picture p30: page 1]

Detail A
Scale: 2:1
Valid for both sides

Swingarm board
Material: Nylon
Scale: 1:2
Note: No cutting edges allowed: 1x45 chamfer on all edges

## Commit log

2020-03-17 Initial commits -> We're working to give more info
    [Oxygen DXF Base (Madera 20mm).dxf, Oxygen DXF Coupling (Madera 20mm).dxf, Oxygen DXF Lateral Derecho (Madera 20mm).dxf, Oxygen DXF Lateral Izquierdo (Madera 20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]
2020-03-23 V5 step and images
    [Oxygen Maker V2 Base.step, Oxygen Maker V2 Contrapeso 1.step, Oxygen Maker V2 Contrapeso 2.step, Oxygen Maker V2 Contrapeso 3.step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]
2020-03-23 Add DXF version files for OxyGEN v5
    [OxyGEN_Maker_V5.dxf]
2020-03-23 Add List of materials for V5
2020-03-30 added new cams
    [1-1 65-205-50-v8.dxf, 1-1 71-205-50-v8.dxf, 1-1 77-205-50-v8.dxf, 1-1 83-205-50-v8.dxf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]
2020-03-31 added assembly tutorial for V5
2020-03-31 renamed some folders and added a 18mm version(thanks to SusoCaamanho)
    [OxyGEN_Maker_V5.dxf, Oxygen DXF Base (Madera 20mm).dxf, Oxygen DXF Coupling (Madera 20mm).dxf, Oxygen DXF Lateral Derecho (Madera 20mm).dxf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]
2020-04-01 renamed some folders and added READMES
    [OxyGEN_Maker_V5.dxf, Oxygen Maker Base.step, Oxygen Maker Contrapeso 1.step, Oxygen Maker Contrapeso 2.step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]
2020-04-01 added new matlab file versions
    [Lleves V7.xlsx]
2020-04-01 added v5m 5mm SLDDRW files
    [BASE.SLDDRW, CONTRAPESO.SLDDRW, COUPLING DENTADO.SLDDRW, COUPLING INFERIOR.SLDDRW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]
2020-04-01 change some folder names
    [1-1 65-205-50-v8.dxf, 1-1 71-205-50-v8.dxf, 1-1 77-205-50-v8.dxf, 1-1 83-205-50-v8.dxf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]
2020-04-02 fixed pdf and slddrw m-v5 'nervio plancha'
    [NERVIO PLANCHA.SLDDRW]
2020-04-02 updated v5-m 5mm step adding screws, washers, nuts and bearings
2020-04-05 added accesories
    [Tube to oval valve.step, spur back to tube.step, tube manometer tube .step, tube to spur valve.step]
2020-04-06 Added IPv1 material's list
2020-04-07 Uploaded IP DXF and STEP metal sheets
    [Oxygen-IP V14.4 Metal Sheet 1 mm Parts.dxf, Oxygen-IP V14.4 Metal Sheet 1 mm Parts.step, Oxygen-IP V14.4 Metal Sheet 3 mm Parts.dxf, Oxygen-IP V14.4 Metal Shee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]
2020-04-07 Added V1 tech info
    Manuales de funcionamiento, premontaje, pautas de contral y proceso de
    ensamblaje
2020-04-08 Updated lightened cams
    [1-1 65-205-50-v8.dxf, 1-1 71-205-50-v8.dxf, 1-1 77-205-50-v8.dxf, 1-1 83-205-50-v8.dxf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]
2020-04-12 Added missed cams
    [1-1 77-205-50-v8.dxf, 1-1 83-205-50-v8.dxf, 1-1 89-205-50-v8.dxf, Levas_1_1.step]
2020-04-12 Fixed 1-3 cams
    [1-1 65-205-50-v8.dxf, 1-1 71-205-50-v8.dxf, 1-1 77-205-50-v8.dxf, 1-1 83-205-50-v8.dxf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]
2020-04-14 Fixed cams name
    [1-2 71-205-50-v8.dxf, 1-2 83-205-50-v8.dxf]
2020-04-14 Added cams STEPs in 3mm
    [Levas_1_1.step, Levas_1_3.step]
2020-04-29 Added pdf to choose the spring arm
2020-04-29 Added more info to choose the spring
2020-05-15 Added cams for v5M
    Special thanks to: @Fluchteugluk
    https://www.linkedin.com/in/hugues-rapinel-599a101b/
    [OXyGEN_V5_M_cams.dxf]
2020-05-30 Added individual DXFs with bend lines
    Added DXFs of the individual sheet metal parts with bend lines on the "Bending" layer.
    [Base.dxf, Central Cover.dxf, Dimmer Support.dxf, Electronics Cover.dxf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]
2020-05-30 Fixed protrusions and hole angles on CAMs
    Fixed small sharp protrusion next to slot on Cams 2XS and 3XS, and changed angle between slot and holes of Cams Set 2 from 61.7 degrees to 60 degrees like Set 1 and 3.
    [1-2 65-205-50-v8.dxf, 1-2 71-205-50-v8.dxf, 1-2 77-205-50-v8.dxf, 1-2 83-205-50-v8.dxf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]
2020-06-03 Added size description to cam filenames
    Added the size description (XL, L, M, S, XS) to the cam filenames to make it easier to know the size of each. The numbers (65, 71, 77, 83, 89) may not mean much to many people.
    [1-1 65-205-50-XL-v8.dxf, 1-1 65-205-50-v8.dxf, 1-1 71-205-50-L-v8.dxf, 1-1 71-205-50-v8.dxf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]
